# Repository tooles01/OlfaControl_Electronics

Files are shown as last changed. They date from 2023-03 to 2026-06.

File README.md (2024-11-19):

# OlfaControl_Electronics

## Full System Overview


<br>

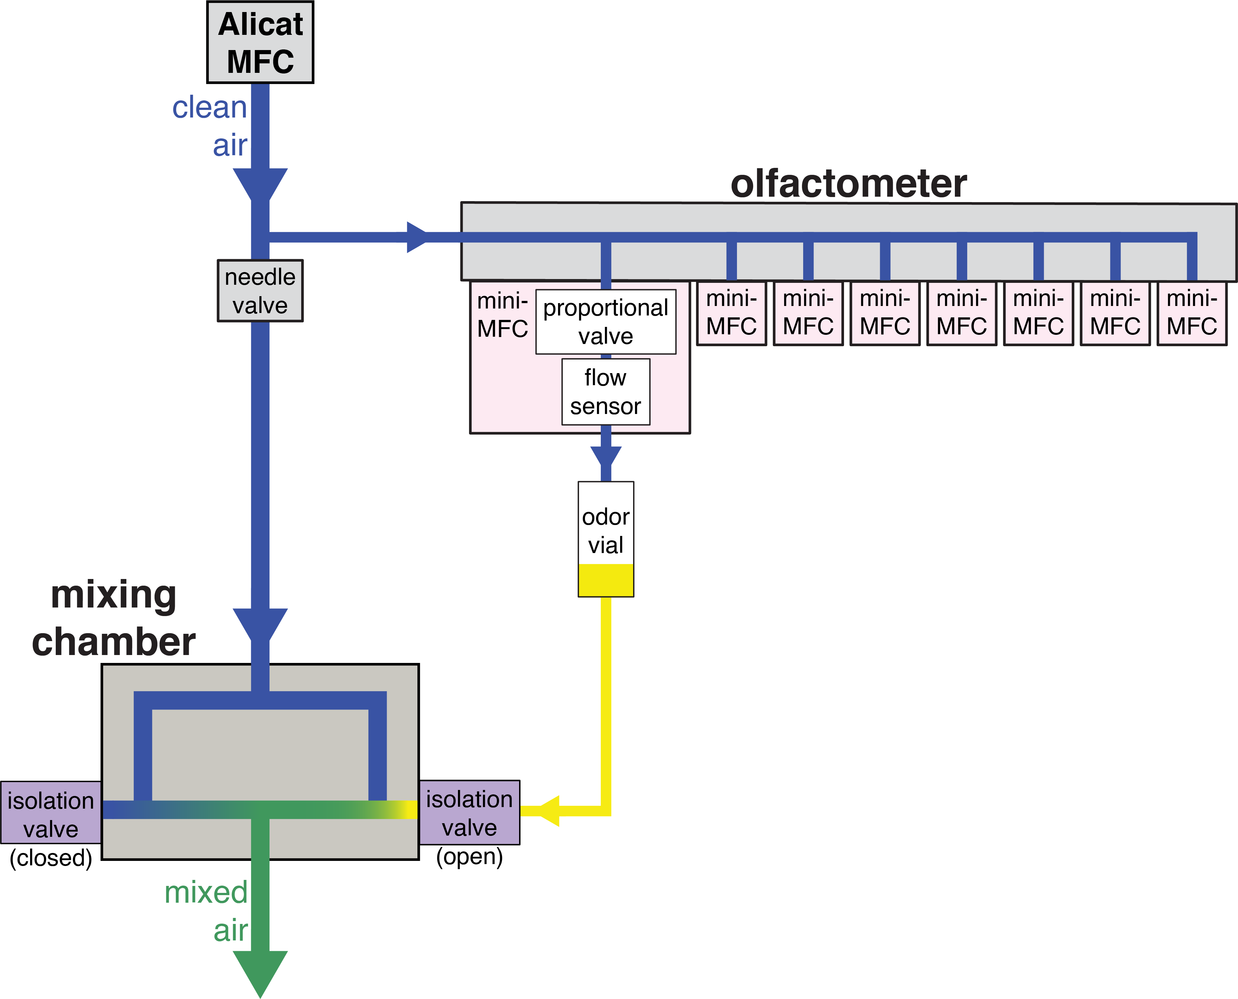
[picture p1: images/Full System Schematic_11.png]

<br>

#### Simplified:

<p align="center">
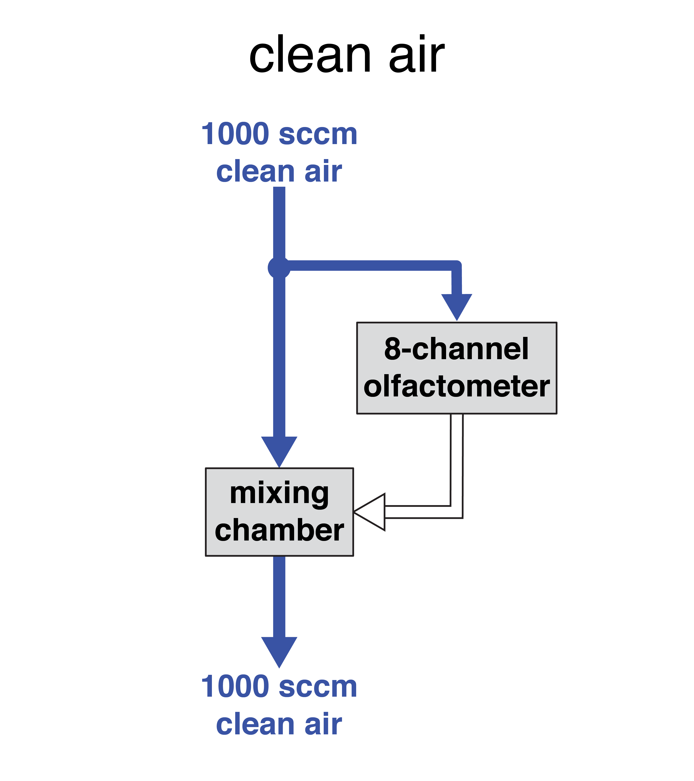
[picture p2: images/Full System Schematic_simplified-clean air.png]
  
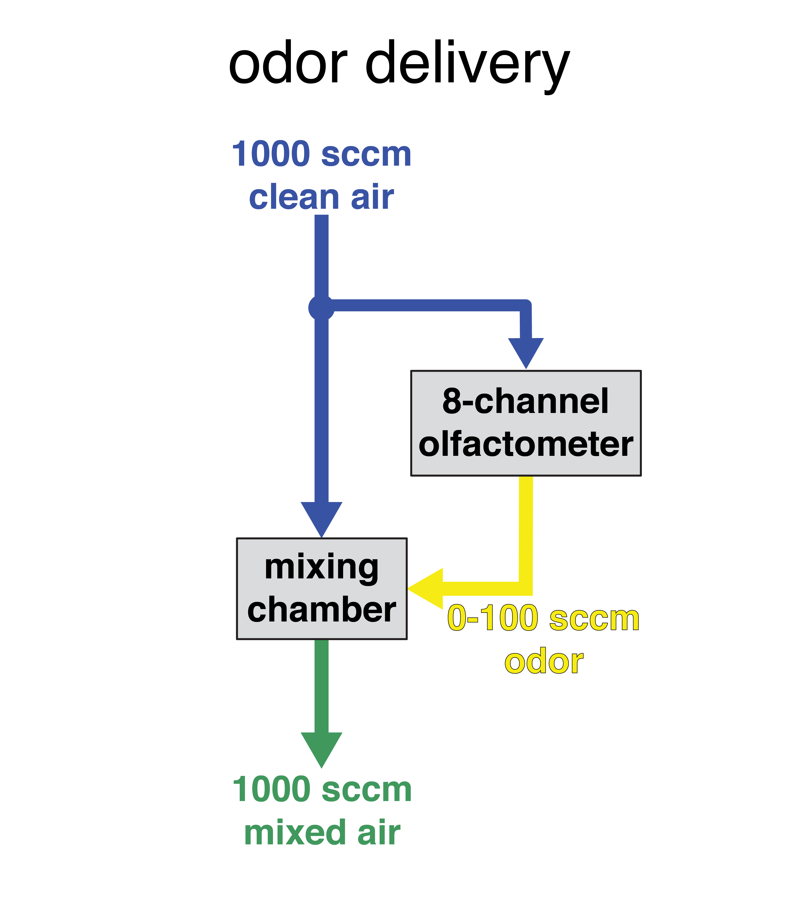
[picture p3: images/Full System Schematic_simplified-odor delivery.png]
  
</p>

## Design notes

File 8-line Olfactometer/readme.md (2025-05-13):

# 8-line Olfactometer

<br>
<p align="left">
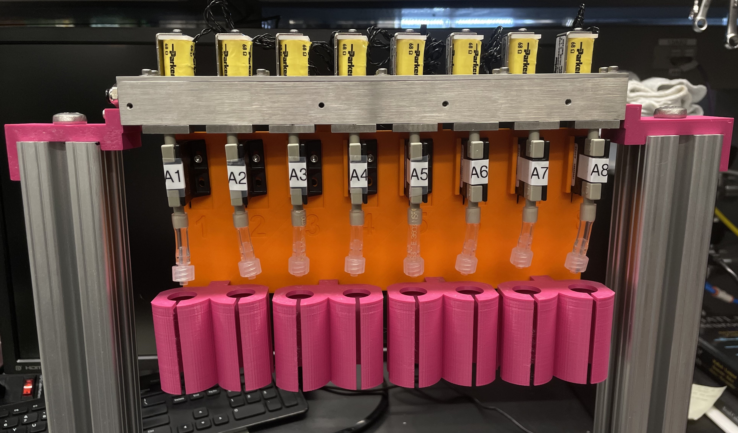
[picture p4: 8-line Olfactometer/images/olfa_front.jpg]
  
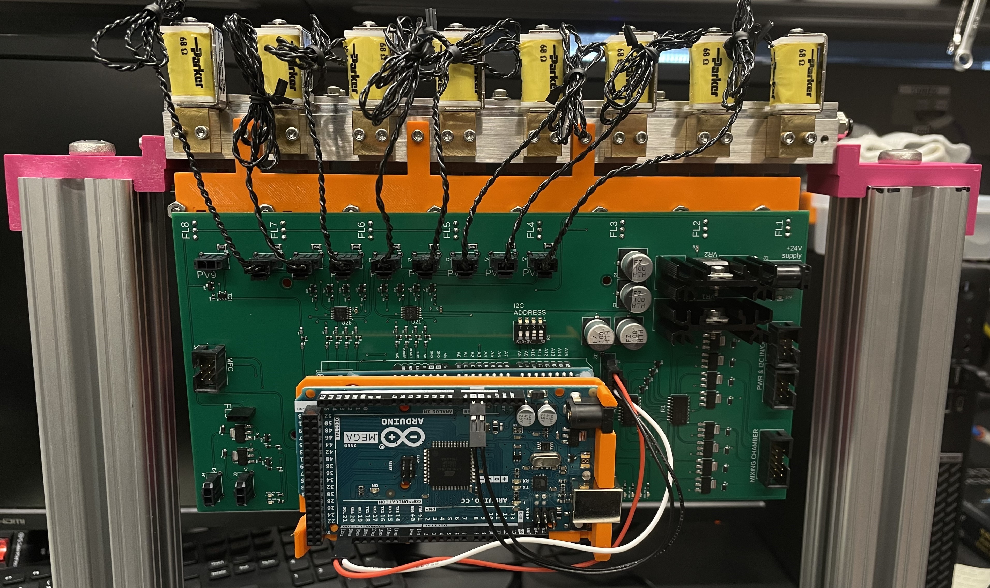
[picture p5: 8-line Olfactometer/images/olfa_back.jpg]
  
</p>

<br>
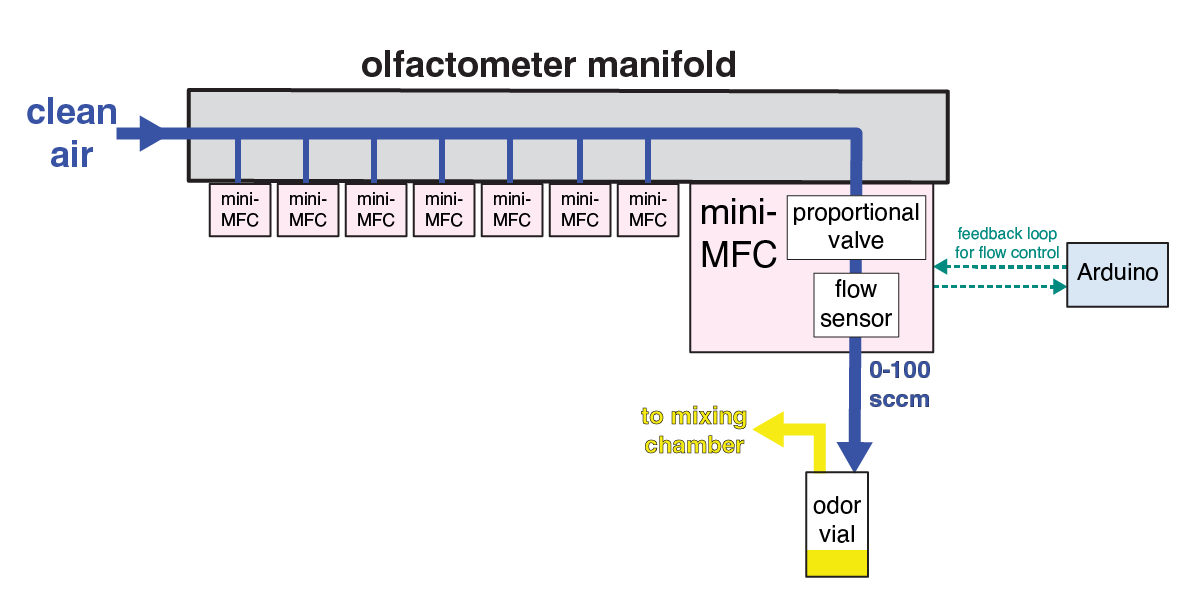
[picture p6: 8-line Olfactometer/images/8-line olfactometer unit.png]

<br>

# Parts to be manufactured
to make a single 8-line unit:
- (x1) top_cover
- (x1) main_manifold_8v
- (x8) main_manifold_cover

<br>

## updates for version 2:
- **main manifold:** mounting holes for main plate on both sides
- **main manifold cover:** 0.01" decrease in length (screw holes are now symmetric)

<br><br>

# Troubleshooting

**Problem:** Inconsistent, "squiggly" odor signal

**Diagnosis:**  Likely something (probably part of the septum) caught in the needle, blocking air flow into the vial

**Solution:** Replace vial input needle

##
**Problem:** Slow odor rise time

**Diagnosis:** Leak

**Solution:** <br>
- Ensure vial cap is on tightly
- Check that isolation valve is completely screwed in
- Replace tubing from vial to mixing chamber

##
**Problem:** Olfactometer not sending back flow values once turned on

**Solution:** <br>
If it is sending back slave addresses:
- Wait 30 seconds or so
- Click "Get Slave Addresses" 1 or 2 times
- If still a problem: Turn 24V power off and back on again, and repeat above steps

If it's not sending back slave addresses:
- Check that PCB is receiving 24V power
- Check that master Arduino I2C pins are correctly connected
- Reupload master Arduino code

##
**Problem:** Zero flow reported, even when proportional valve signal is at max (255)

**Solution:** Replace proportional valve

<!-- Troubleshooting Section as Table-->
<!--
# Troubleshooting

### Hardware/PID testing:

| Problem | Diagnosis | Solution |
| ----------- | ----------- | ----------- |
| Inconsistent, "squiggly" odor signal from PID | Likely something (probably part of the septum) caught in the needle, blocking air flow into the vial | Replace vial input needle |
| Odor signal from one line is significantly higher/lower than others | Variety of possible issues | Check if flow sensor is hitting desired setpoint. <li>If no: Recalibrate flow sensor.</li><li>If yes: Replace proportional valve</li><br>If problem persists, check for leaks.|| Slow odor rise time | Leak | <li>Ensure vial cap is on tightly.</li><li>Replace tubing from vial to mixing chamber.</li><li>Check that isolation valve is completely screwed into mixing chamber.</li>|

<br>

### Electronics/GUI:

| Problem | Solution |
| ----------- | ----------- |
| Olfactometer not sending back flow values once turned on | If it is sending back slave addresses: <li>Wait 30 seconds or so</li><li>Click "Get Slave Addresses" 1 or 2 times</li><li>If still a problem: Turn 24V power off and back on again, and repeat above steps</li><br>If it's not sending back slave addresses: <li>Check that PCB is receiving 24V power</li> <li>Check that master Arduino I2C pins are correctly connected</li><li>Re-upload master Arduino code</li>|
| Zero flow reported from flow sensor, even when proportional valve signal is at max (255) | Replace proportional valve |
-->

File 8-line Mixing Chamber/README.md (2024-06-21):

# Clippard Mixing Chamber

<p align="center">
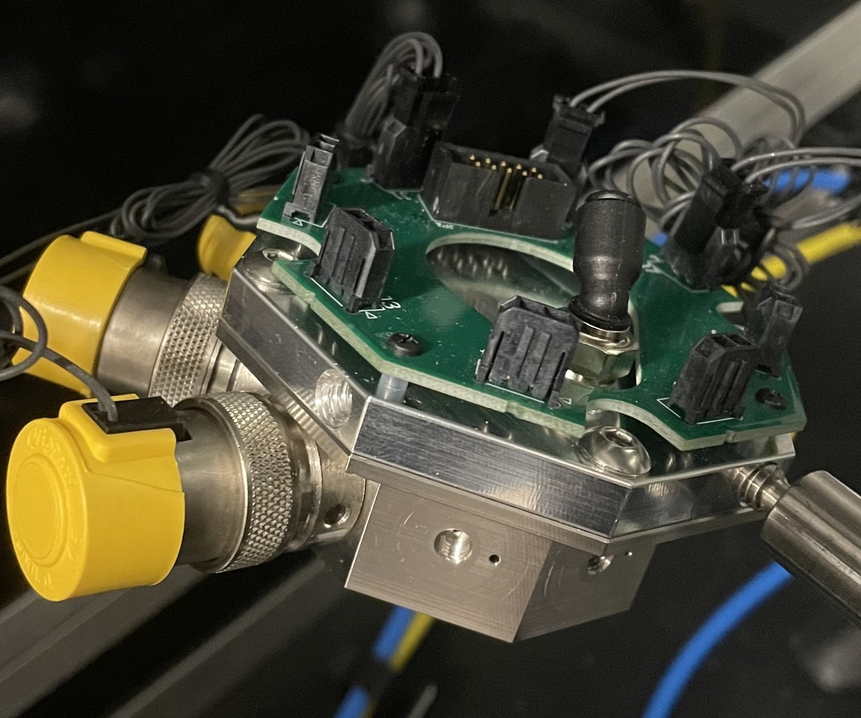
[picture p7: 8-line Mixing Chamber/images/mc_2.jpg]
  
</p>

<br>

<p align="center">
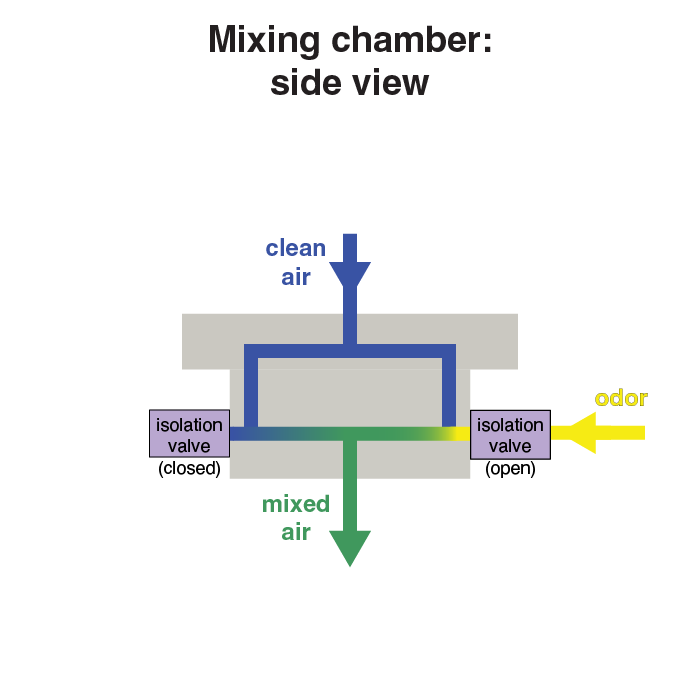
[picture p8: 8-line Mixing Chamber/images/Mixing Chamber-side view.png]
  
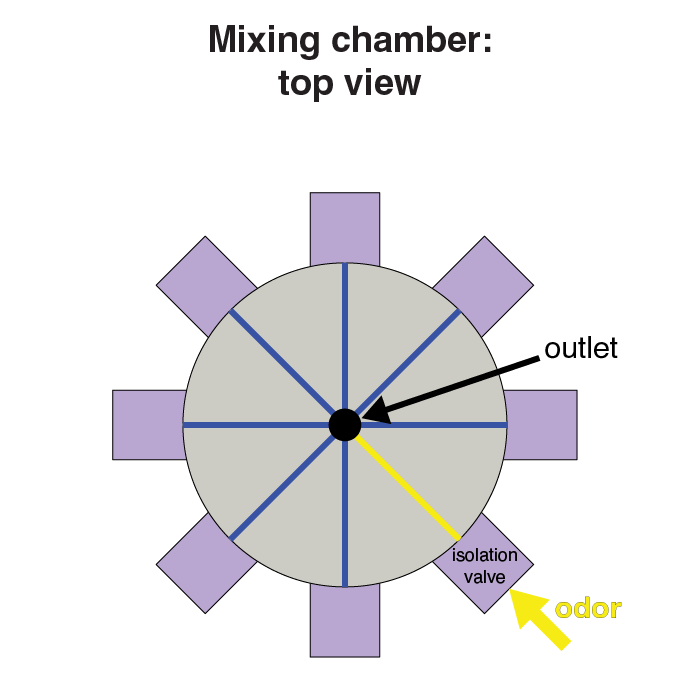
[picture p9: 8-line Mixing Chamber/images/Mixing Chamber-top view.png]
  
</p>

<br>

<p align="left">
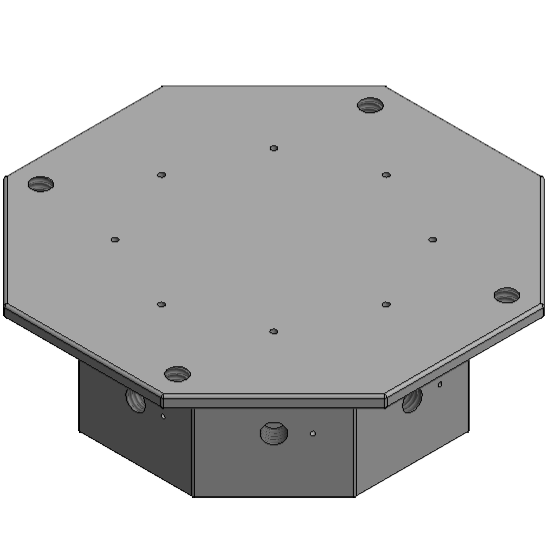
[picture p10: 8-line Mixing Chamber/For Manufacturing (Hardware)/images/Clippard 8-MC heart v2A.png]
  
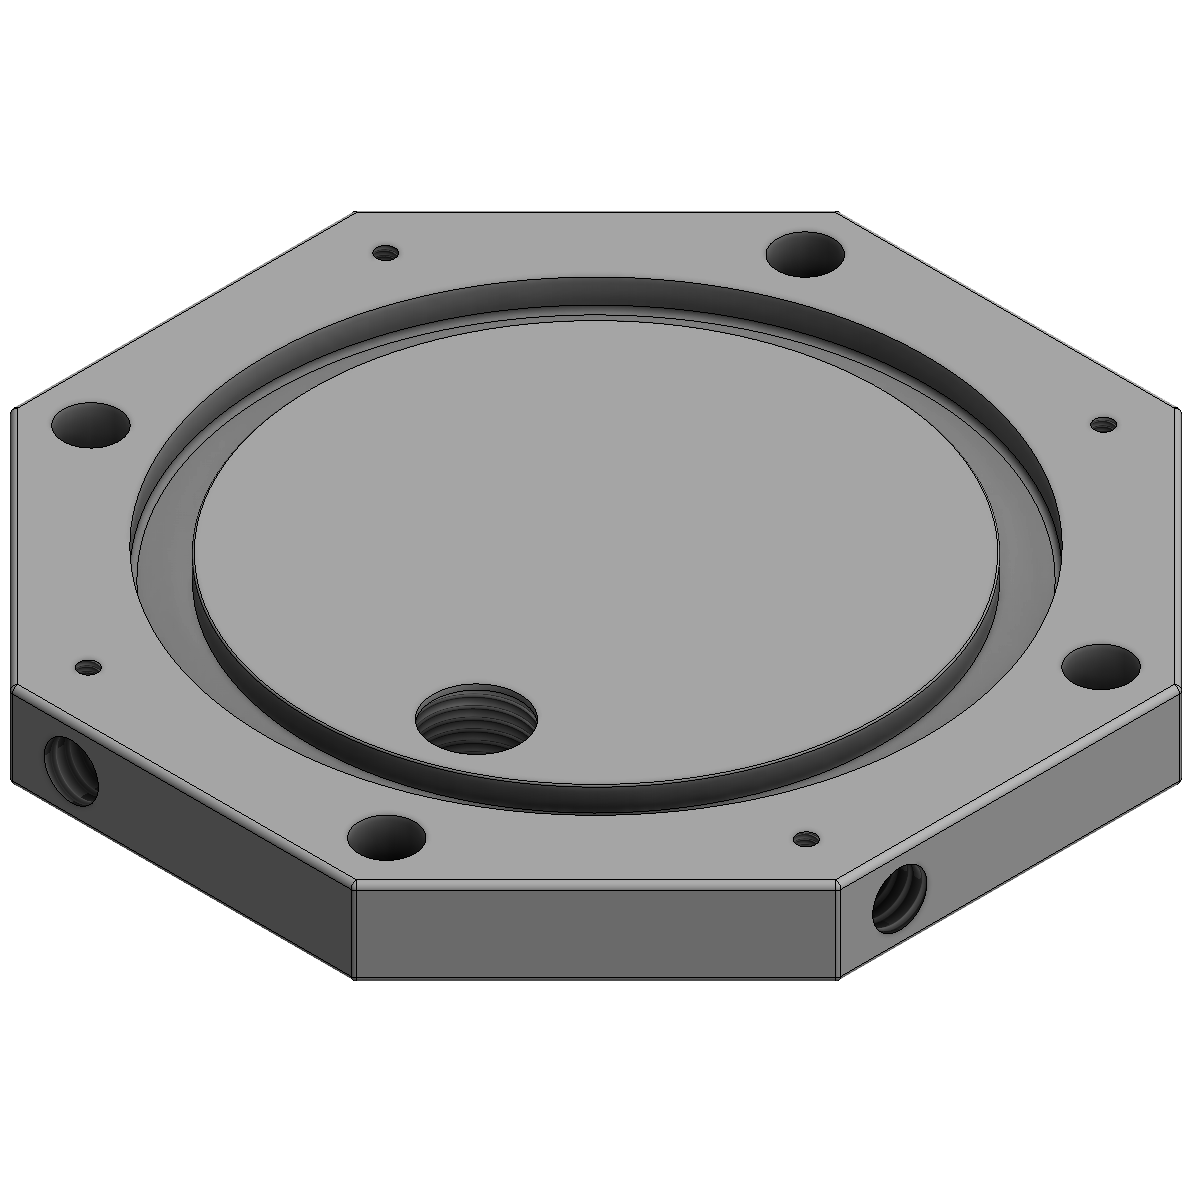
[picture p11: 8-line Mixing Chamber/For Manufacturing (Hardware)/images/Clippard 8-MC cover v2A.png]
  
</p>

<br><br>

# Parts to be manufactured

to make a single unit:

- (x1) Clippard 8-MC cover
- (x1) Clippard 8-MC heart

<br><br>

## updates for version 2:
- **Clippard 8-MC cover**
    - Slightly different location of PCB mounting holes
- **Clippard 8-MC heart**
    - Removed bottom depression, outlet changed from a male thread to an NResearch (1/4-28) female hole (matches the vial inlet holes)
    - Odor (vial) inlet ID changed
    - Odor input hole (from the bottom) was previously not aligned with its connecting inlet hole (horizontal) - tied geometries together

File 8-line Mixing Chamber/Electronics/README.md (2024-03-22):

# Clippard 8-line Mixing Chamber

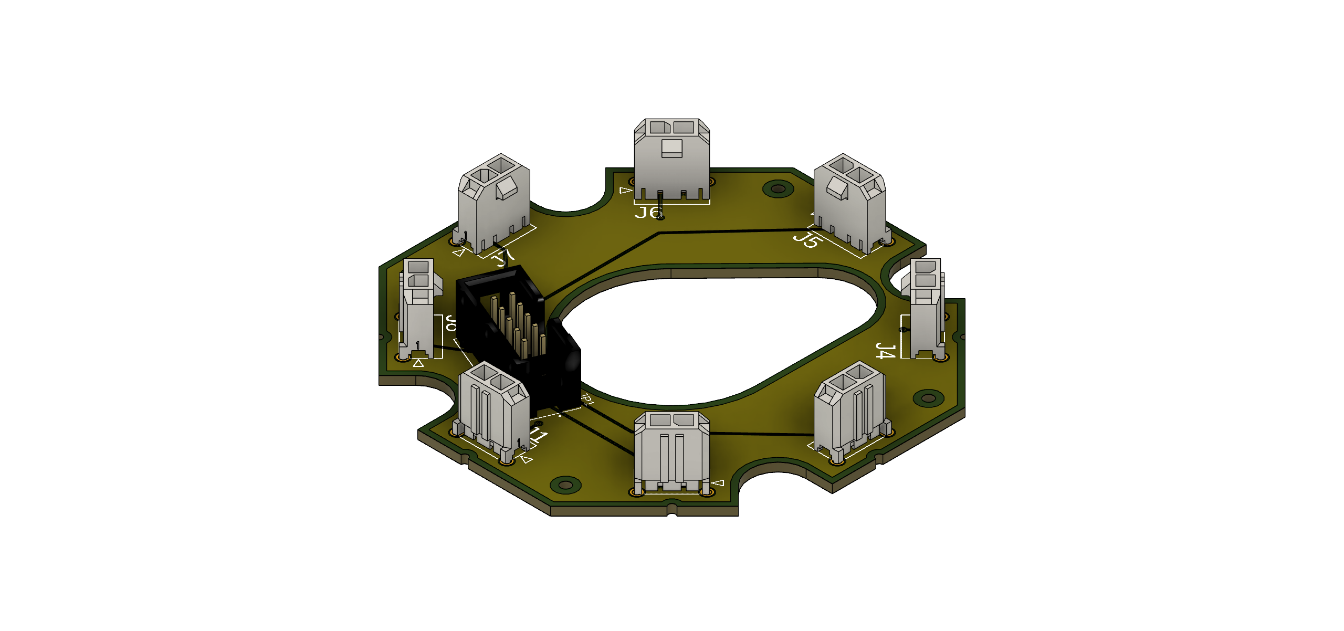
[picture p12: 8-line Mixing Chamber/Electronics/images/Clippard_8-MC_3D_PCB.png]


To be used with 8-line Olfactometer PCB (MAIN_CNTRL_v02).

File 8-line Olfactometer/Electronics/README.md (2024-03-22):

# 8-line Olfactometer

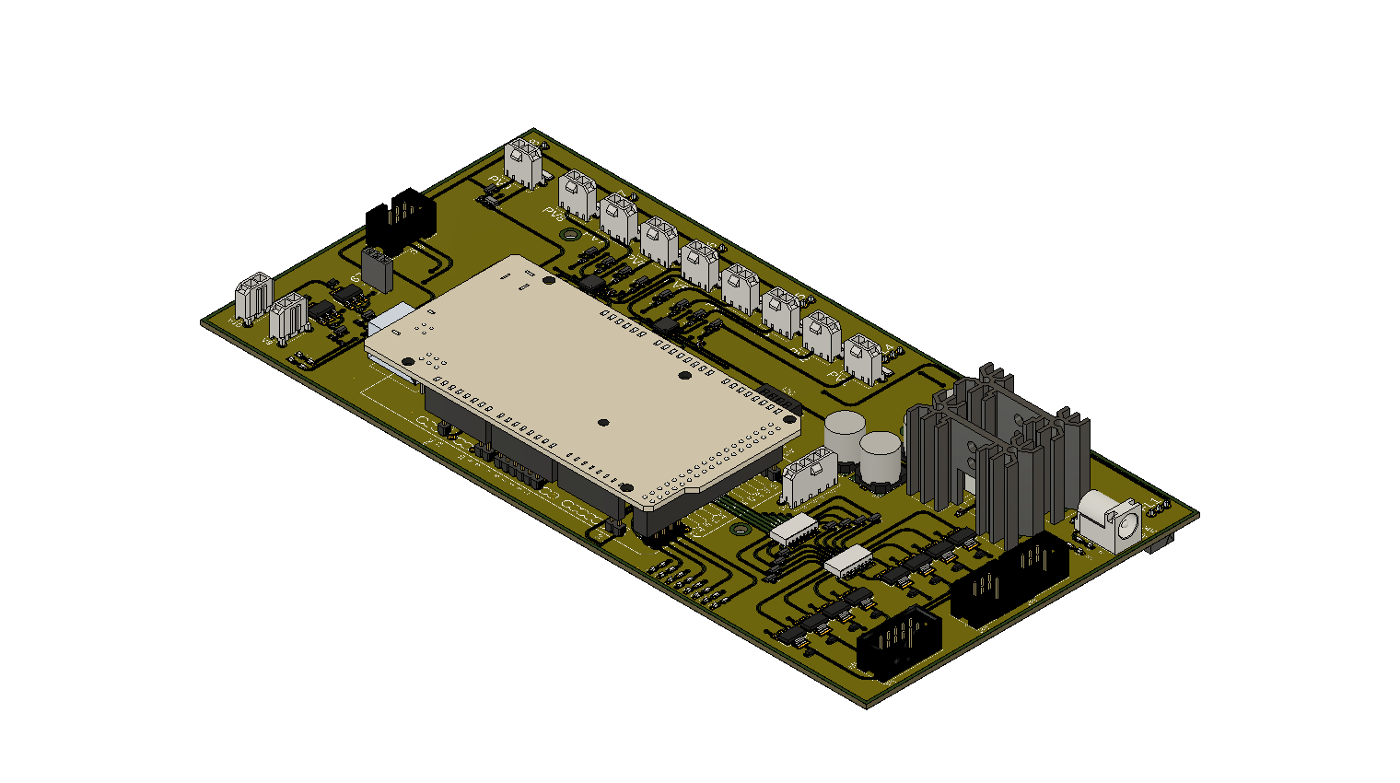
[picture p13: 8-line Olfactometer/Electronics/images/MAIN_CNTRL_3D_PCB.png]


## PCB Assembly
- Attach (x2) heat sinks to VR1 and VR2 using (x2) 4-40 x 1/4" screw and hex nut
- Solder Arduino header pins onto PCB
- Set I2C address on S1 (full dictionary of addresses is currently stored in master.ino source code)
- Connect master Arduino
    - Make a wire to connect from J2 (4pos Molex female) to master Arduino pins (Dupont male wires). Connect to SDA, SCL, GND and GND.
    - (Mount master Arduino on top using Arduino holder 3D printed part)

<br><br><br>

## updates for version 2:

### power:
- single 24V power supply (instead of 1x 24V supply and 1x 10V supply)
    - voltage regulators & corresponding circuitry to shift down to 10V for the components that need it
    - (2 voltage regulators + heat sinks to prevent overheating when multiple lines activated at once)

### error fixes:
- fixes (x4) incorrectly wired proportional valves
- removes connection between isolation valves 3 & 8

### other:
- multiple boards can be chained together by a single ribbon cable, which carries the power and I2C lines
    - (only 1 board in the chain needs a 24V input, the rest receive power through the ribbon cable)
- updated header for connecting to mixing chamber (standard 10pos IDC cable)

### new components:
- (x8) LEDs to indicate isolation valve activated
- (x2) LEDs to indicate power (10V, 24V)
- (x1) connection for additional flow sensor
- (x1) connection for additional proportional valve
- (x2) connection for additional isolation valve
- (x1) connection for Alicat MFC

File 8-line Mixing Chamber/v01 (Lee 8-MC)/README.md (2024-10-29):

# Lee Mixing Chamber

<p align="left">
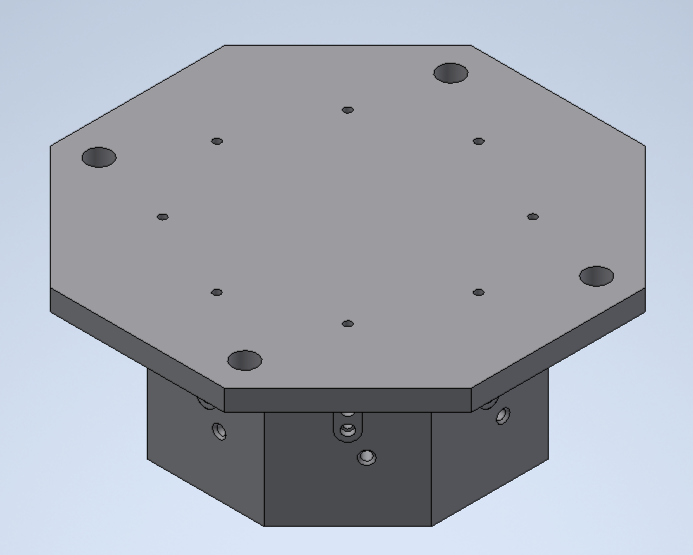
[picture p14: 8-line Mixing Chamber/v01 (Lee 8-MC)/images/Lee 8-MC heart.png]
  
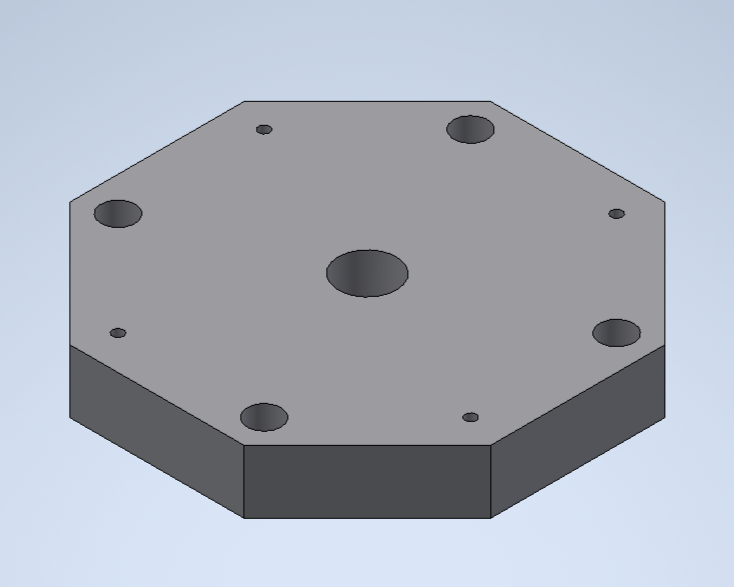
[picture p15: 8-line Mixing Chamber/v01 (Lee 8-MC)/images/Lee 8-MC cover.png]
  
</p>

<br><br>

# Parts to be manufactured

to make a single unit:

- (x1) Lee 8-MC cover
- (x1) Lee 8-MC heart

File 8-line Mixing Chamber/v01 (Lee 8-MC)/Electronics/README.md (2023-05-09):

# Lee 8-line Mixing Chamber

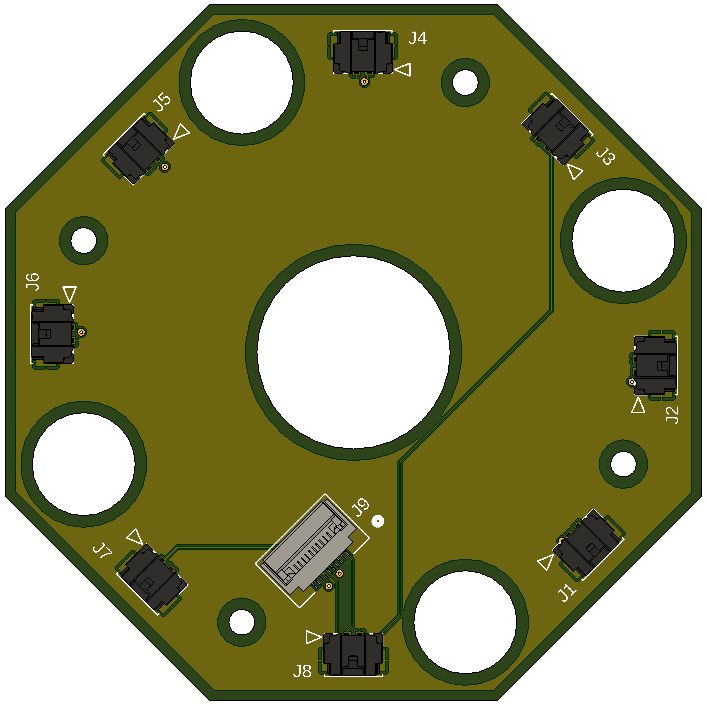
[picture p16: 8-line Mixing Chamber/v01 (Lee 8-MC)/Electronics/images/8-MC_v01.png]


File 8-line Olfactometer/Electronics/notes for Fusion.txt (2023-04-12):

Fusion file names:

MAIN CNTRL v01

schematic:	MAIN CNTRL_v3 v8
board:		MAIN_CNTRL_v3_v217
3D PCB:		MAIN_CNTRL_v3 v140
screenshot:	MAIN_CNTRL_v3 v140

MAIN CNTRL V02

schematic:	MAIN_CNTRL_v2_v166
board:		MAIN CNTRL_v2 v183
3D PCB:		MAIN CNTRL_v2 v14
screenshot:	MAIN CNTRL_v2 v14

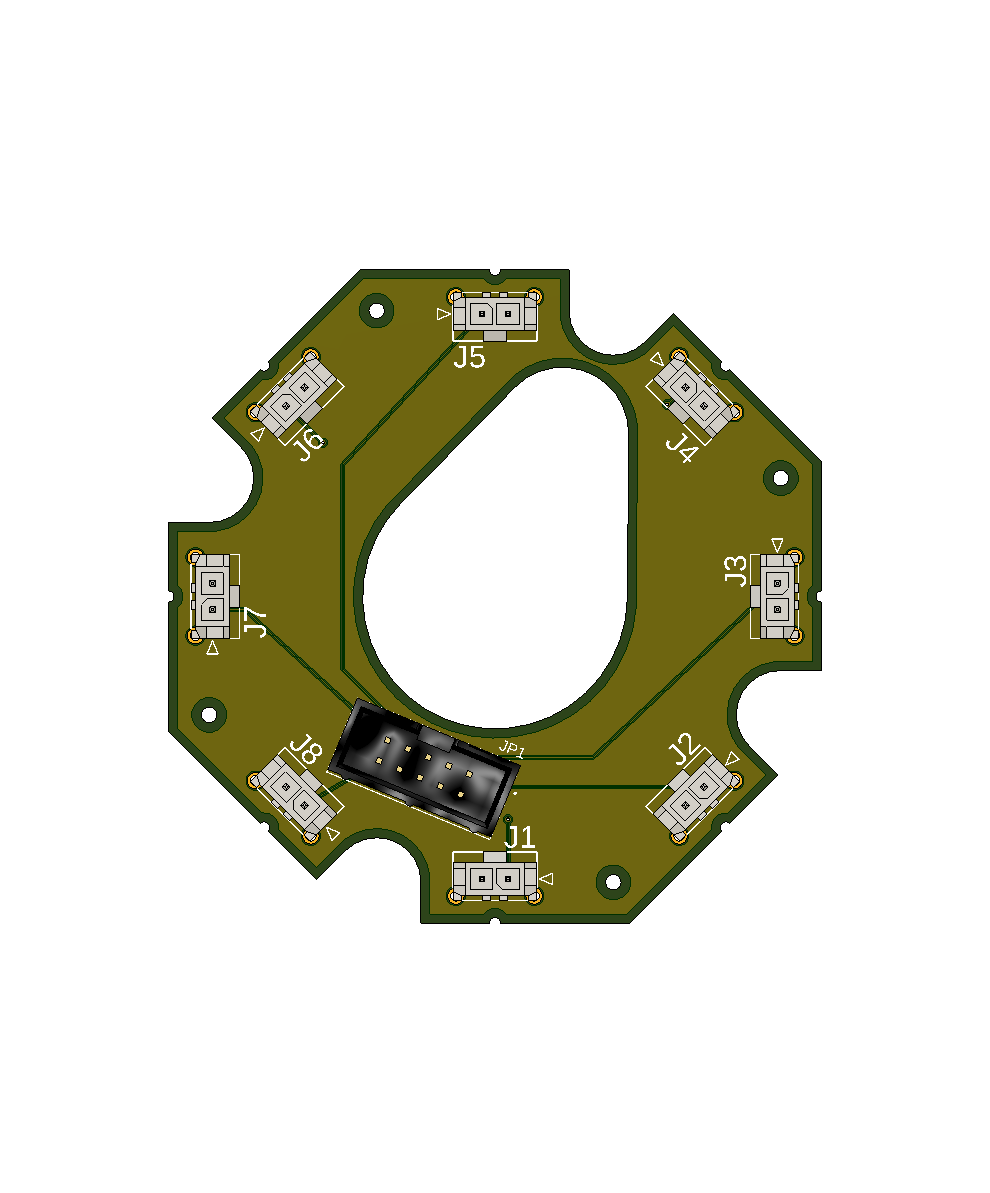
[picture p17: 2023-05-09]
8-line Mixing Chamber/Electronics/images/Clippard 8-MC 3D PCB_top.png

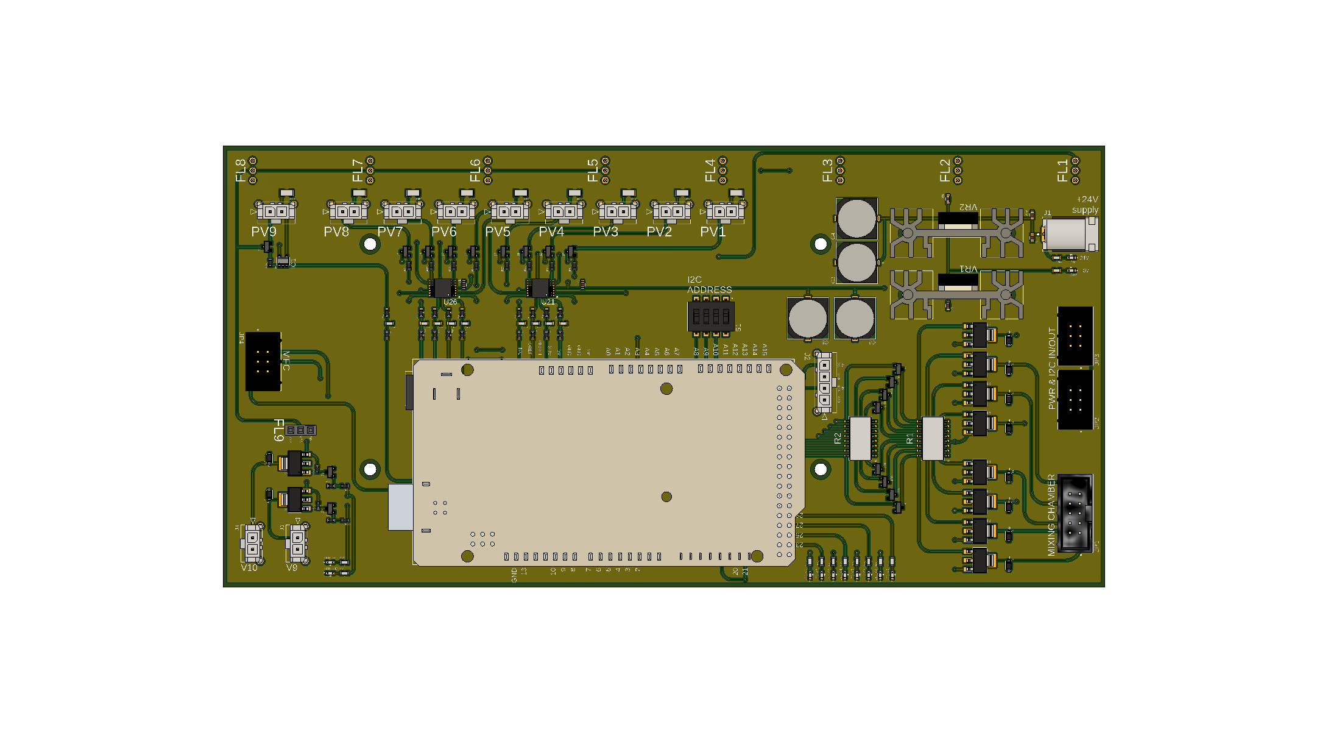
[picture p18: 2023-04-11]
8-line Olfactometer/Electronics/images/MAIN CNTRL 3D PCB_top.png

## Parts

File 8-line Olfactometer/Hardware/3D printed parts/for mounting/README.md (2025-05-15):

### for mounting with sliding or standing setup
Hole (for mounting with standing setup) will fit M8 or 5/16" screw

<br>

<!--BigAssembly_01_8020_1515.iam-->
**mount_bracket 8020_1515_withhole**  
Fits on 1.5" profiles from 8020
<p align="center">
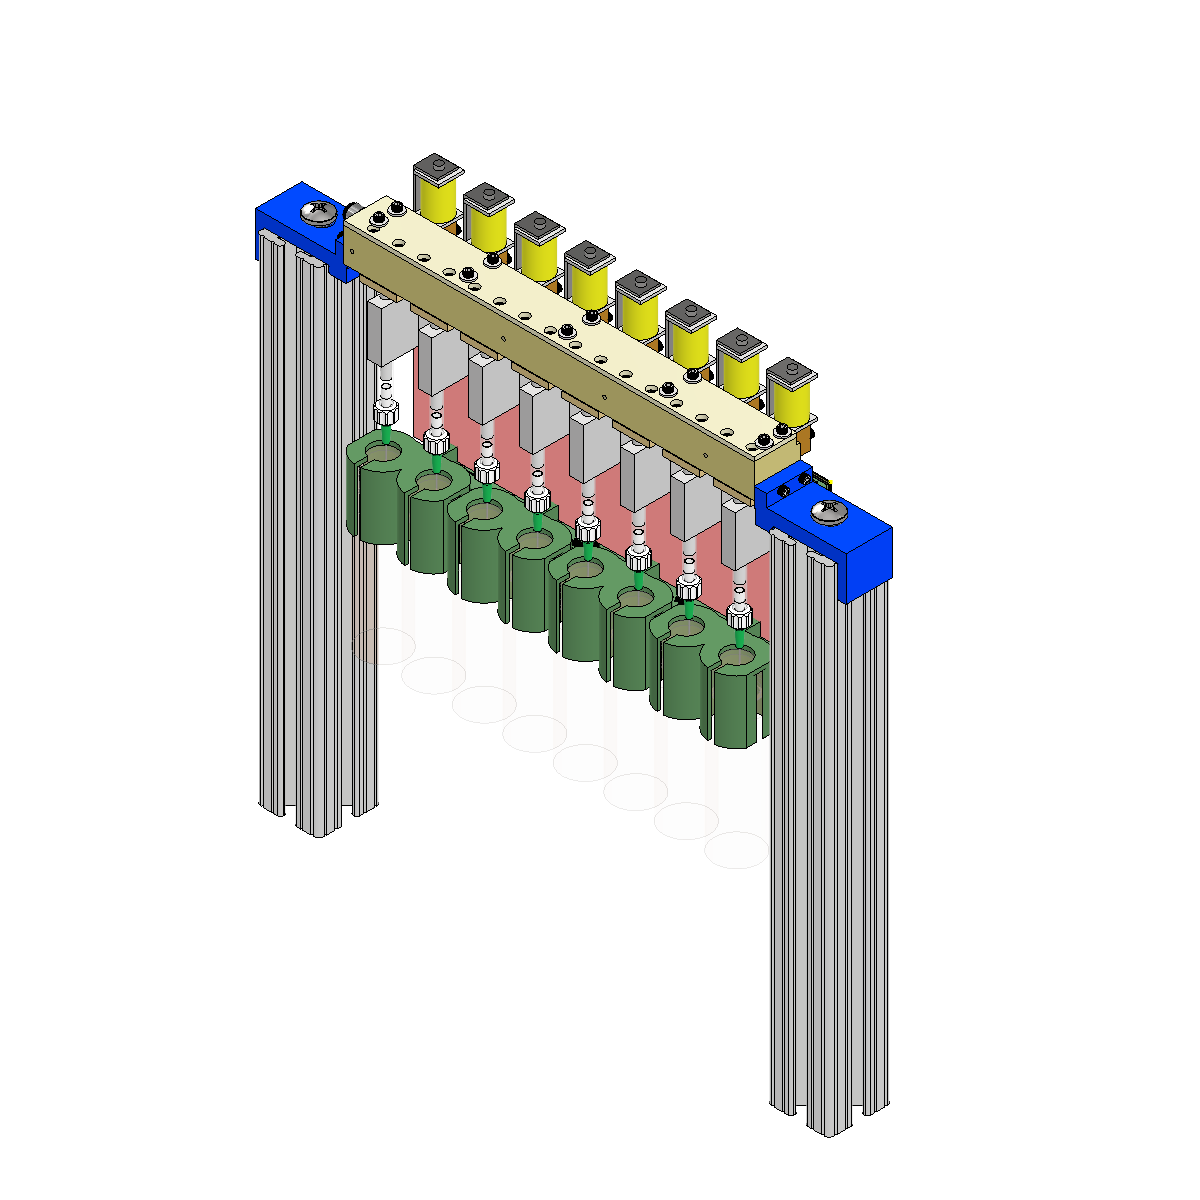
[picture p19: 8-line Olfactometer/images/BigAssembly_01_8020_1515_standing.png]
  
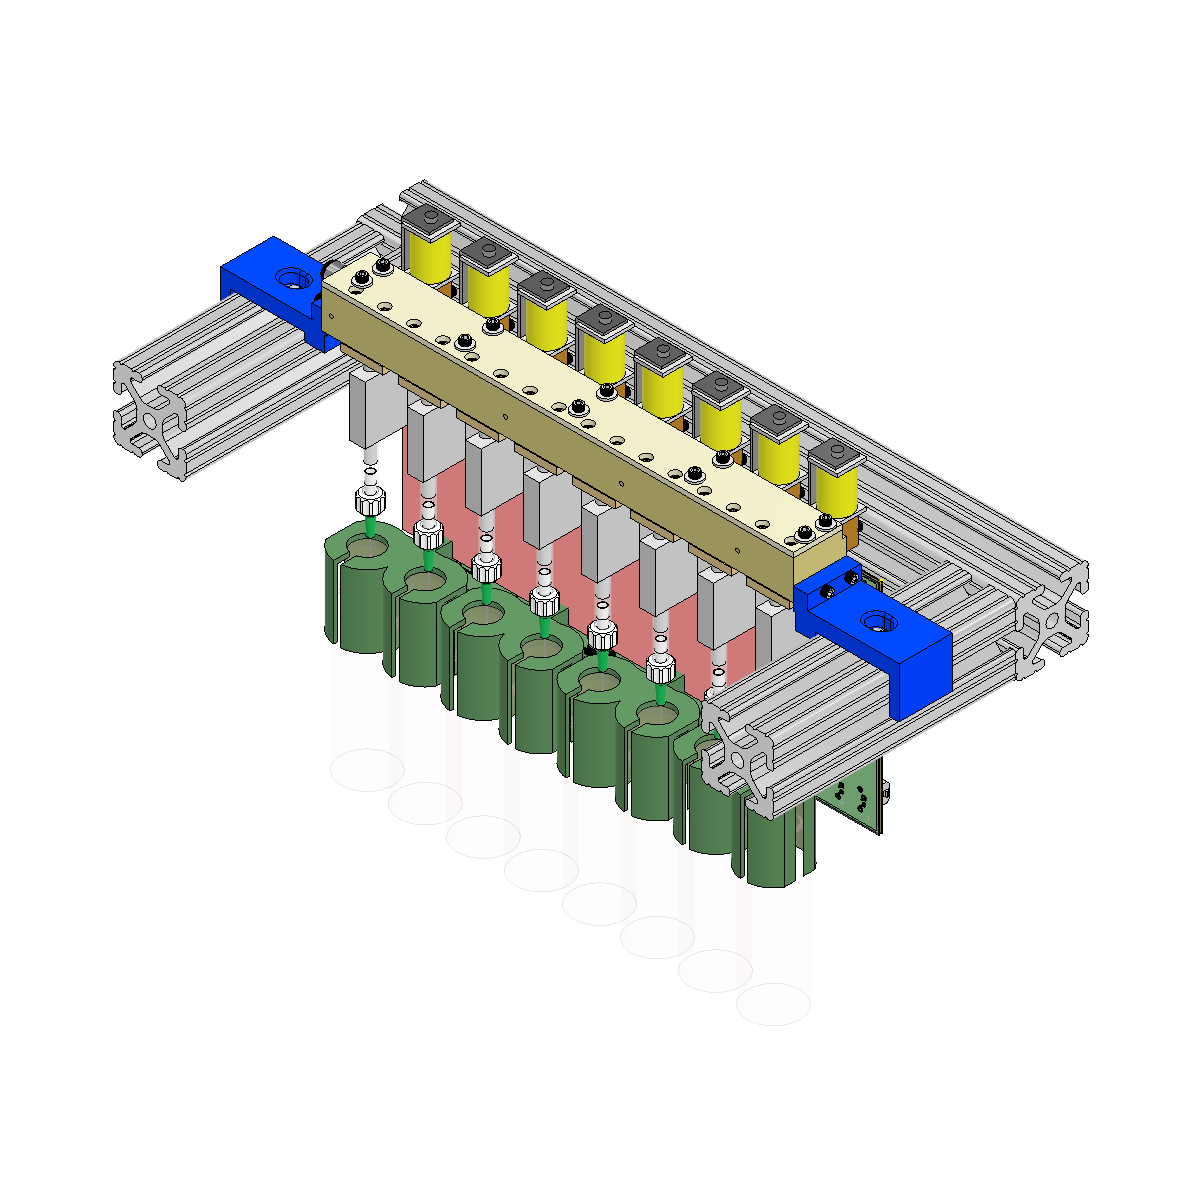
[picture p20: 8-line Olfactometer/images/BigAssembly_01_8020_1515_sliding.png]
  
</p>
<br>

<!--BigAssembly_01_item_8.iam-->
**mount_bracket item_8_withhole**  
Fits on 40mm profiles from item
<p align="center">
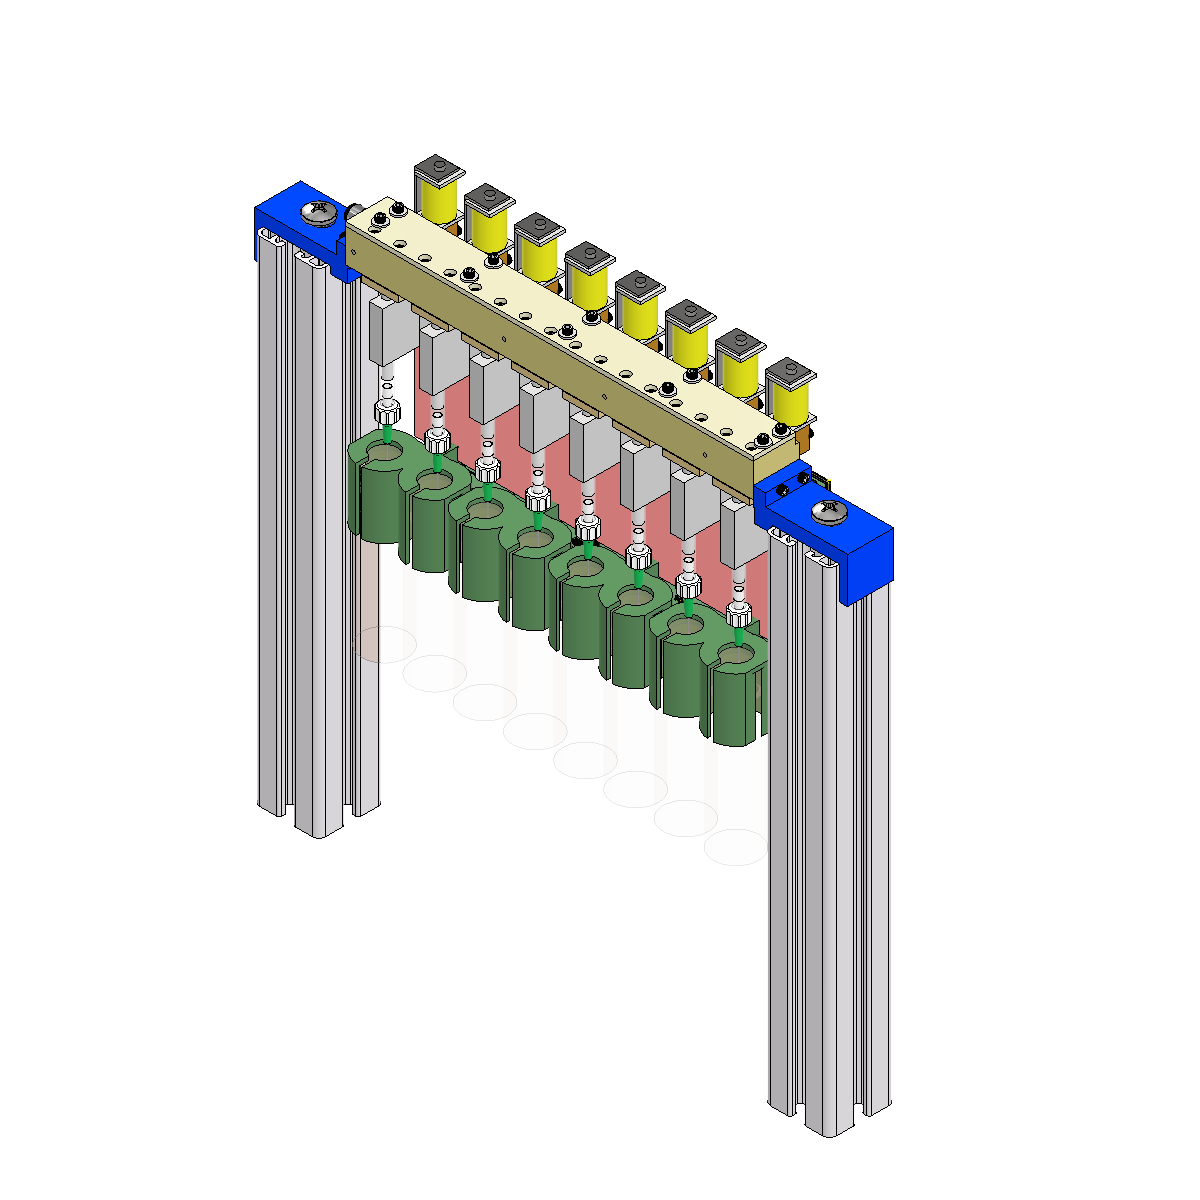
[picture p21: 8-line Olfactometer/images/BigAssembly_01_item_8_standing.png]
  
</p>
<!--
## TODO:
- add sliding setup for item
- add links to item and 8020 profiles
-->

#
### Current setup in Mainland lab:
<!--BigAssembly_02.iam-->
**mount_left**  
**mount_right**  
Mounted using 40mm profiles from item, M8 screws

<p align="center">
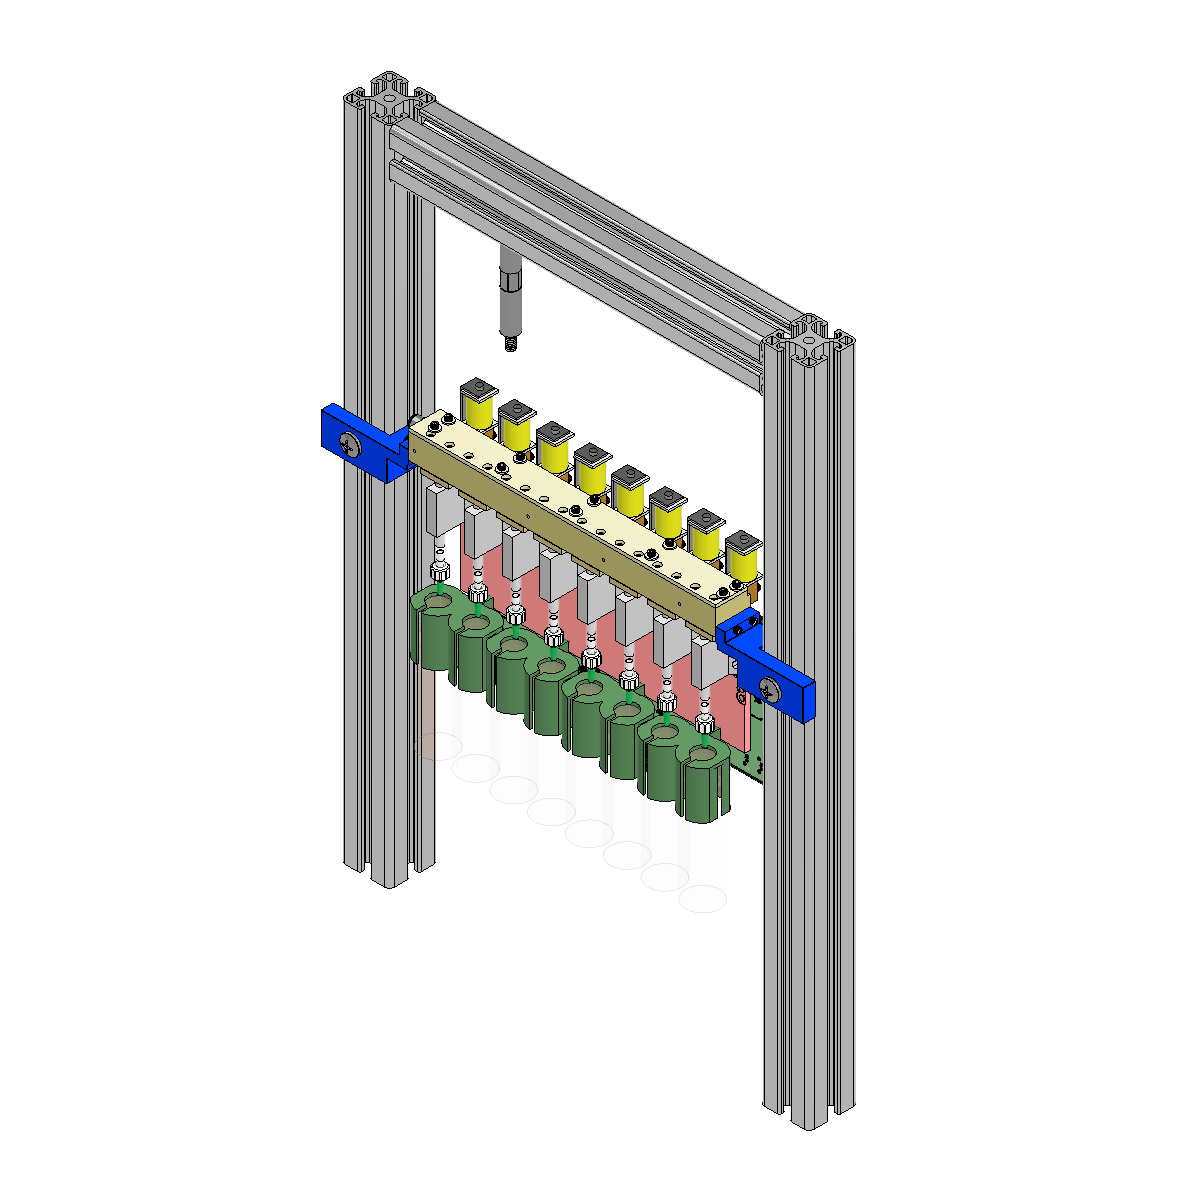
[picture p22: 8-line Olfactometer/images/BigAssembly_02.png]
  
</p>

<!-- 
For mounting with sliding setup only:

**mount_bracket 8020_1515**
Fits on 1.5" profiles from 8020

**mount_bracket item_5**
Fits on 20mm profiles from item
-->

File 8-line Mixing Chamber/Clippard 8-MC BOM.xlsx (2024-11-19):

Item # | Qty |  | Description | Manufacturer | Manuf. Part #
1 | 1 | Clippard 8-MC heart v2A | Clippard 8-valve Mixing Chamber Heart | Custom Machined Part | n/a
2 | 1 | Clippard 8-MC cover v2A | Clippard 8-valve Mixing Chamber Cover | Custom Machined Part | n/a
3 | 1 | #227 O-ring | O-ring for sealing MC heart & cover | McMaster-Carr | 5267T193 (https://www1.mcmaster.com/5267T193/)
4 | 1 | Input fitting | 1/8 NPT x 1/8" Tube OD Push-To-Connect Fitting | McMaster-Carr | 5779K102 (https://www1.mcmaster.com/5779K102/)
5 | 8 | Isolation valves | Clippard 24V Isolation Valves | Clippard | EV-2M-24-V (https://www.clippard.com/part/EV-2M-24-V)
6 | 4 | 10-24 x 1/2" screws | 18-8 Stainless Steel Button Head Hex Drive Screw 10-24 Thread Size, 1/2" Long | McMaster-Carr | 92949A242 (https://www1.mcmaster.com/92949A242/)
7 | 1 | Clippard 8-MC PCB | Clippard 8-valve Mixing Chamber PCB | Custom PCB | n/a
8 | 4 | 1/8" spacers | Off-White Nylon Unthreaded Spacer 1/8" OD, 1/8" Long, for Number 2 Screw Size | McMaster-Carr | 94639A460 (https://www1.mcmaster.com/94639A460/)
9 | 4 | 2-56 x 1/4"screws | Nylon Pan Head Screws Phillips, 2-56 Thread, 1/4" Long | McMaster-Carr | 94735A707 (https://www1.mcmaster.com/94735A707-94735A124/)

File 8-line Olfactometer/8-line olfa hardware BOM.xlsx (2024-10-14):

 | Item # | Qty |  | Description | Manufacturer | Part # | cost / pack | pack size
main manifold to top cover | 6 | 1 | Input fitting | Push-to-Connect Tube Fitting for Air; Straight Adapter, for 1/4" Tube OD x 1/8 NPT Male | McMaster-Carr | 5779K108 (https://www1.mcmaster.com/5779K108/) | $5.49 | each
 | 1 | 1 | main_manifold_8v_v02 | 8-line Olfactometer Main Manifold | Custom Machined Part | n/a
 | 2 | 1 | top_cover_02 | 8-line Olfactometer Top Cover | Custom Machined Part | n/a
 | 3 | 1 | #051 O-ring | Chemical-Resistant Viton® Fluoroelastomer O-Ring; 1/16 Fractional Width, Dash Number 051 | McMaster-Carr | 9464K721 (https://www1.mcmaster.com/9464K721/) | $16.61 | each | * ordered -051 size, might be -052 tho
 | 4 | 10 | 4-40 x 1/4" screws | 18-8 Stainless Steel Socket Head Screw 4-40 Thread Size, 1/4" Long | McMaster-Carr | 92196A106 (https://www1.mcmaster.com/92196A106/) | $3.92 | 100 pack
 | 5 | 10 | 4-40 washers | 18-8 Stainless Steel Washer for Number 4 Screw Size, 0.125" ID, 0.312" OD | McMaster-Carr | 92141A005 (https://www1.mcmaster.com/92141A005/) | $1.43 | 100 pack
prop valves to main manifold | 7 | 8 | Proportional Valves | VSO Low Flow Miniature Proportional Valve | Parker | 910-000200-002
 | 8 | 16 | FKM O-rings | O-ring, FKM, 0.114" ID x 0.070" Thick | Parker | 190-007024-002
 | 9 | 16 | 4-40 x 5/8" screws | Screw 4-40 x 5/8" Pan Head | Parker | 191-000115-010
main plate | 10 | 1 | mainPlate | Main Plate for mounting olfactometer | 3D printed | n/a
 | 11 | 3 | 4-40 x 1/4" screw | 18-8 Stainless Steel Socket Head Screw 4-40 Thread Size, 1/4" Long | McMaster-Carr | 92196A106 (https://www1.mcmaster.com/92196A106/) | $5.74 | 100 pack
flow sensors | 12 | 8 | Flow Sensors | Air Flow Sensor 200sccm Male, 0.2" (5.08mm) Plastic | Honeywell | AWM3100V
 | 13 |  | 1/8" ID 1/4" OD tubing | 1/8" ID x 1/4" OD x 1/16" Wall Tygon® S3™ E-3603 Laboratory Tubing | United States Plastic Corp. | 57631 | $9.50 | 10 feet
 | 14 | 8 | Male luer to 1/8" barb | Idex Barbed Luer Adapter, Polypropylene, 0.080" Bore, Female Luer Lock x 1/8" Hose Barb | IDEX | P-859 (https://www.coleparmer.com/i/idex-barbed-luer-adapter-polypropylene-0-080-bore-female-luer-lock-x-1-8-hose-barb-1-ea/0202406?searchterm=p-859) | $1.30 | each
 | 15 | 8 | #008 O-rings | Chemical-Resistant Viton® Fluoroelastomer O-Ring 1/16 Fractional Width, Dash Number 008 | McMaster-Carr | 9464K13 (https://www1.mcmaster.com/9464K13/) | $8.50 | 100 pack
 | 16 | 8 | main_manifold_cover_1v_v02 | 8-line Olfactometer Main Manifold Cover | Custom Machined Part | n/a
 | 17 | 16 | 4-40 x 7/8" screws | 18-8 Stainless Steel Socket Head Screw 4-40 Thread Size, 7/8" Long | McMaster-Carr | 92196A114 (https://www1.mcmaster.com/92196A114/) | $7.88 | 100 pack
 | 18 | 8 | 4-40 x 3/8" screws | 18-8 Stainless Steel Socket Head Screw 4-40 Thread Size, 3/8" Long | McMaster-Carr | 92196A108 (https://www1.mcmaster.com/92196A108/) | $6.07 | 100 pack
 | 19 | 8 | 4-40 hex nuts | 18-8 Stainless Steel Hex Nut 4-40 Thread Size | McMaster-Carr | 91841A005 (https://www1.mcmaster.com/91841A005/) | $3.89 | 100 pack
for mounting | 20 | 2 | 3d printed mount |  | 3D printed | n/a
 | 21 | 4 | 4-40 x 1/2" screws | 18-8 Stainless Steel Socket Head Screw 4-40 Thread Size, 1/2" Long | McMaster-Carr | 92196A110 (https://www1.mcmaster.com/92196A110/) | $6.38 | 100 pack
 | 22 | 2 | M8 screws
vial holders | 23 | 4 | vialHolder_2v | Vial Holder | 3D printed | n/a
 | 24 | 4 | 4-40 Heat-set inserts | Tapered Heat-Set Inserts for Plastic 4-40 Thread Size, 0.135" Installed Length, Brass | McMaster-Carr | 93365A120 (https://www1.mcmaster.com/93365A120/) | $14.11 | 100 pack
 | 25 | 4 | 4-40 x 3/8" screws | 18-8 Stainless Steel Socket Head Screw 4-40 Thread Size, 3/8" Long | McMaster-Carr | 92196A108 (https://www1.mcmaster.com/92196A108/) | $6.07 | 100 pack
flow sensor to vial | 26 | 8 | 21G Needles | PrecisionGlide Hypodermic Needle 21gx2" Green | Becton-Dickinson | 305129 (https://www.henryschein.com/us-en/medical/p/medical-surgical-supplies/hypodermic-supplies/needle-disposable/9879426) | $20.00 | 100/Bx
vial to mixing chamber | 27 | 8 | Odor Vials | Precleaned Volatile Organic Analyte Sampling Vials, 40 mL, 24-400 Screw-Thread | Restek | 21797 (https://www.restek.com/p/21797) | $122.00 | 72 pack
 | 28 | 8 | Fittings & Ferrules | 1/4-28 Two Piece Fitting Set | NResearch | 252P109 (https://www.nresearch.com/) | $161.68 | 50 pack
 | 29 | 8 | 1/32" ID x 1/16" OD tubing | Masterflex® Transfer Tubing, PTFE, 1/32" ID x 1/16 " OD | Masterflex | 06407-41 (https://us.vwr.com/store/item/NA5133589/masterflex-transfer-tubing-polytetrafluoroethylene-ptfe-avantor)

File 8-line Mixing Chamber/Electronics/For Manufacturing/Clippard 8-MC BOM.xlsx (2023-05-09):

Item # | Designator | Qty | Manufacturer | Mfg Part # | Description / Value | Package / Footprint | Type | Instructions / Notes
1 | JP1 | 1 | TE Connectivity AMP Connectors | 1761681-3 | Connector Header Through Hole 10 position 0.100 (2.54mm)" |  | Through Hole
2 | J1, J2, J3, J4, J5, J6, J7, J8 | 8 | Molex | 0436500215 | Connector Header Through Hole 2 position 0.118 (3.00mm)" |  | Through Hole

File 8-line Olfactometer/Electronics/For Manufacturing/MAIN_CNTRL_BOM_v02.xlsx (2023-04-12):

Item # | Designator | Qty | Manufacturer | Mfg. Part # | Distributor | Distrib. Part # | Description | Package/Footprint | Type | Notes
1 | C1, C2, C7, C8 | 4 | TDK Corporation | CGA3E2X7R1H104M080AD | Digi-Key | 445-9834-1-ND | Capacitor 0.1 µF ±20% 50V Ceramic Capacitor | 0603 (1608 Metric) | Surface Mount
2 | C3, C4, C5, C6 | 4 | Rubycon | 50THV100M10X10.5 | Digi-Key | 1189-2059-1-ND | Capacitor 100 µF ±20% 50V Aluminum Electrolytic Capacitor | Radial, Can - SMD | Surface Mount
3 | C9, C10 | 2 | TDK | CGA3E2X7R1H103K080AE | Digi-Key | 445-15955-1-ND | Capacitor 10000 pF ±10% 50V Ceramic Capacitor | 0603 (1608 Metric) | Surface Mount
4 | D1, D2, D3, D4, D5, D6, D7, D8, D9, D10 | 10 | ROHM Semiconductor | RB168VYM150FHTR | Digi-Key | RB168VYM150FHCT-ND | Diode Schottky 150 V 1A | 2-SMD, Flat Lead | Surface Mount
5 | FL1, FL2, FL3, FL4, FL5, FL6, FL7, FL8, FL9 | 9 | Sullins Connector Solutions | PPPC031LFBN-RC | Digi-Key | S7036-ND | 3 Position Header Connector 0.100 (2.54mm) Through Hole Gold" |  | Through Hole
6 | HS1, HS2 | 2 | Assmann WSW Components | V8813W | Digi-Key | AE10771-ND | Heat Sink SOT-32, TO-220, TOP-3 Aluminum Board Level, Vertical |  | Through Hole
7 | IC1 | 1 | STMicroelectronics | TS321AILT | Digi-Key | 497-8093-1-ND | General Purpose Amplifier 1 Circuit | SOT-23-5 | Surface Mount
8 | J1 | 1 | CUI Devices | PJ-037AH | Digi-Key | CP-037AH-ND | DC Power Jack Connector 2.0 x 6.5 mm, 5.0 A |  | Through Hole
9 | JP2, JP3, JP4 | 3 | TE Connectivity AMP Connectors | 1761681-1 | Digi-Key | A122759-ND | Connector Header Through Hole 6 position 0.100 (2.54mm)" |  | Through Hole
10 | J2 | 1 | Molex | 436500415 | Digi-Key | WM1919-ND | Connector Header Through Hole 4 position 0.118 (3.00mm)" |  | Through Hole
11 | J3, J4 | 2 | Molex | 436500215 | Digi-Key | WM1917-ND | Connector Header Through Hole 2 position 0.118 (3.00mm)" |  | Through Hole
12 | LED1, LED2 | 2 | Vishay Semiconductor Opto Division | VLMG1300-GS08 | Digi-Key | VLMG1300-GS08CT-ND | LED Indication Green 571nm | 0603 (1608 Metric) | Surface Mount
13 | X1 | 1 |  |  |  |  |  |  |  | DNI
14 | PV1, PV2, PV3, PV4, PV5, PV6, PV7, PV8, PV9 | 9 | Molex | 436500215 | Digi-Key | WM1917-ND | Connector Header Through Hole 2 position 0.118 (3.00mm)" |  | Through Hole
15 | R1, R2 | 2 | Bourns Electronics | 4816P-1-103LF | Digi-Key | 4816P-1-103LFCT-ND | Resistor 10k Ohm ±2% 160mW Power Per Element Isolated 8 Resistor Network/Array | 16-SOIC (0.220, 5.59mm Width)" | Surface Mount
16 | R3 | 1 | Bourns Electronics | 4816P-1-102LF | Digi-Key | 4816P-1-102LFCT-ND | Resistor 1k Ohm ±2% 160mW Power Per Element Isolated 8 Resistor Network/Array | 16-SOIC (0.220, 5.59mm Width)" | Surface Mount
17 | R4, R9, R20, R22, R24, R29, R40, R42, R65 | 9 | Vishay Dale | CRCW12062R20FKEA | Digi-Key | 541-2.20FFCT-ND | Resistor 2.2 Ohms ±1% 0.25W | 1206 (3216 Metric) | Surface Mount
18 | R5, R10, R21, R23, R25, R30, R41, R43, R54, R57, R66 | 11 | Panasonic | ERJPA3F1001V | Digi-Key | P1.0KBYCT-ND | Resistor 1 kOhms ±1% 0.333W | 0603 (1608 Metric) | Surface Mount
19 | R52 | 1 | Vishay | RCS06031K20FKEA | Digi-Key | 541-10435-1-ND | Resistor 1.2 kOhms ±1% 0.25W | 0603 (1608 Metric) | Surface Mount
20 | R53 | 1 | Vishay Dale | RCS0603470RFKEA | Digi-Key | 541-10469-1-ND | Resistor 470 Ohms ±1% 0.25W | 0603 (1608 Metric) | Surface Mount
21 | R55, R56, R58, R59 | 4 | Panasonic | ERJ-PA3F1002V | Digi-Key | P10KBYCT-ND | Resistor 10 kOhms ±1% 0.333W | 0603 (1608 Metric) | Surface Mount
22 | R6, R11, R14, R17, R26, R31, R34, R37, R62 | 9 | Yageo | SR0603FR-7T100KL | Digi-Key | YAG5821CT-ND | Resistor 100 kOhms ±1% 0.25W | 0603 (1608 Metric) | Surface Mount
23 | R7, R12, R15, R18, R27, R32, R35, R38, R63 | 9 | Yageo | SR0603FR-7T2K2L | Digi-Key | YAG5834CT-ND | Resistor 2.2 kOhms ±1% 0.25W | 0603 (1608 Metric) | Surface Mount
24 | R8, R13, R16, R19, R28, R33, R36, R39, R44, R45, R46, R47, R48, R49, R50, R51, R60, R61, R64 | 19 | Vishay | RCS0603120RFKEA | Digi-Key | 541-10426-1-ND | Resistor 120 Ohms ±1% 0.25W | 0603 (1608 Metric) | Surface Mount
25 | S1 | 1 | TE Connectivity | 1-1825059-7 | Digi-Key | 1-1825059-7-ND | SPST Flush Slide Sealed 2.54 mm Pitch Surface Mount DIP Switch |  | Surface Mount
26 | U1, U2, U3, U4, U5, U6, U7, U8, U28, U30 | 10 | Diodes Incorporated | ZXMP7A17GQTA | Digi-Key | ZXMP7A17GQTADICT-ND | MOSFET P-Channel | SOT223 | Surface Mount
27 | U21, U26 | 2 | Texas Instruments | LM324KAPWR | Digi-Key | 296-18449-1-ND | General Purpose Amplifier 4 Circuit | 14-TSSOP (0.173, 4.40mm Width)" | Surface Mount
28 | U9, U10, U11, U12, U13, U14, U15, U16, U17, U18, U19, U20, U22, U23, U24, U25, U27, U29, U31 | 19 | Infineon Technologies | IRLML6244TRPBF | Digi-Key | IRLML6244TRPBFCT-ND | MOSFET N-Channel | Micro3 (SOT-23) | Surface Mount
29 | LED_V1, LED_V2, LED_V3, LED_V4, LED_V5, LED_V6, LED_V7, LED_V8, LED_V9, LED_V10 | 10 | Vishay Semiconductor Opto Division | VLMB1300-GS08 | Digi-Key | VLMB1300-GS08CT-ND | LED Indication Blue 470nm | 0603 (1608 Metric) | Surface Mount
30 | VR1, VR2 | 2 | STMicroelectronics | L78S10CV | Digi-Key | 497-6039-5-ND | Linear Voltage Regulator IC Positive Fixed 1 Output 2A | TO-220 | Through Hole
31 | JP1 | 1 | TE Connectivity AMP Connectors | 1761681-3 | Digi-Key | 1761681-3-ND | Connector Header Through Hole 10 position 0.100 (2.54mm)" |  | Through Hole

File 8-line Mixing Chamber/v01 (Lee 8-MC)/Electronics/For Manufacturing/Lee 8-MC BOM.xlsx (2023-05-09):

Item # | Designator | Qty | Manufacturer | Mfg Part # | Description / Value | Package / Footprint | Type | Instructions / Notes
1 | J9 | 1 | Hirose | FH52-10S-0.5SH | 10 Position FFC, FPC Connector Contacts, Bottom 0.020" (0.50mm) Surface Mount, Right Angle |  | Surface Mount
2 | J1, J2, J3, J4, J5, J6, J7, J8 | 8 | Molex Connector Corporation | 5055670281 | Connector Header Surface Mount, Right Angle 2 position 0.049" (1.25mm) |  | Surface Mount

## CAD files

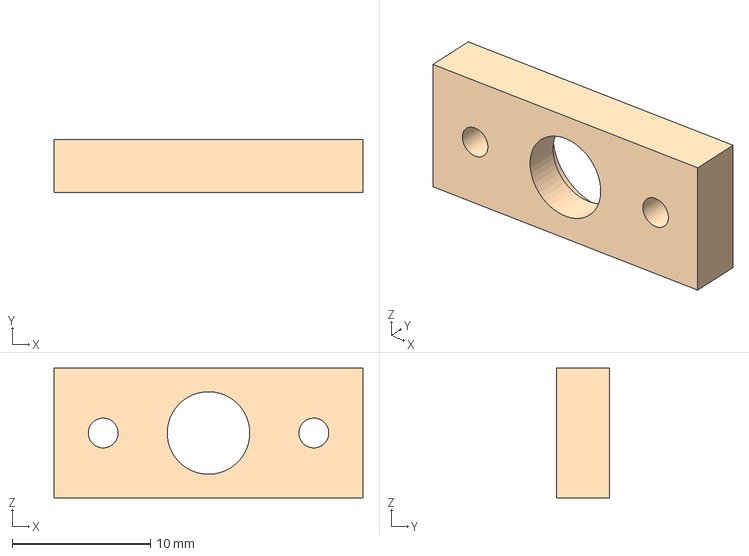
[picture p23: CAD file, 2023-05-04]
8-line Olfactometer/Hardware/For Manufacturing/CAD files/main_manifold_cover_1v_v02.stp
22.4 x 3.81 x 9.40 mm

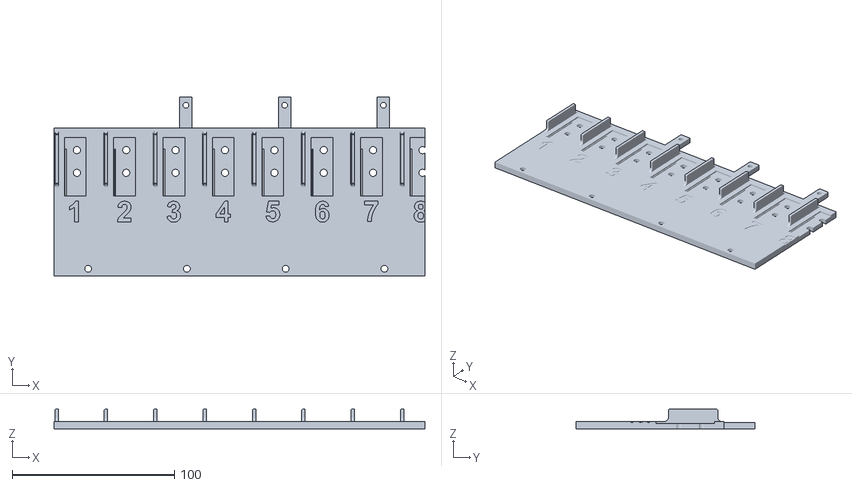
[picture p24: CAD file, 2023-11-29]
8-line Olfactometer/3D printed parts/mainPlate.stl
229.0 x 110.5 x 12.2

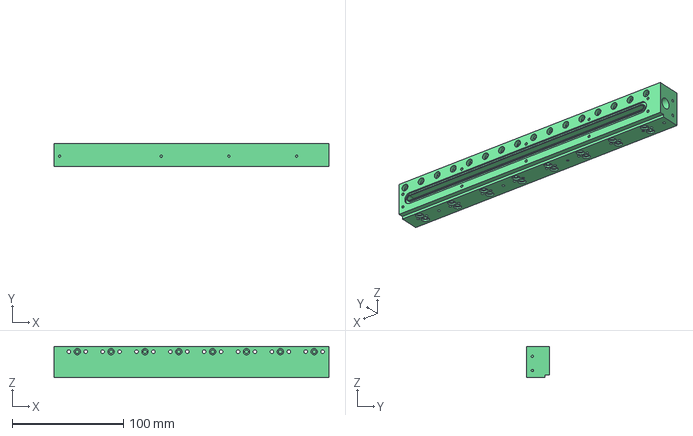
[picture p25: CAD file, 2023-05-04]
8-line Olfactometer/Hardware/For Manufacturing/CAD files/main_manifold_8v_v02.stp
247.6 x 20.3 x 27.9 mm

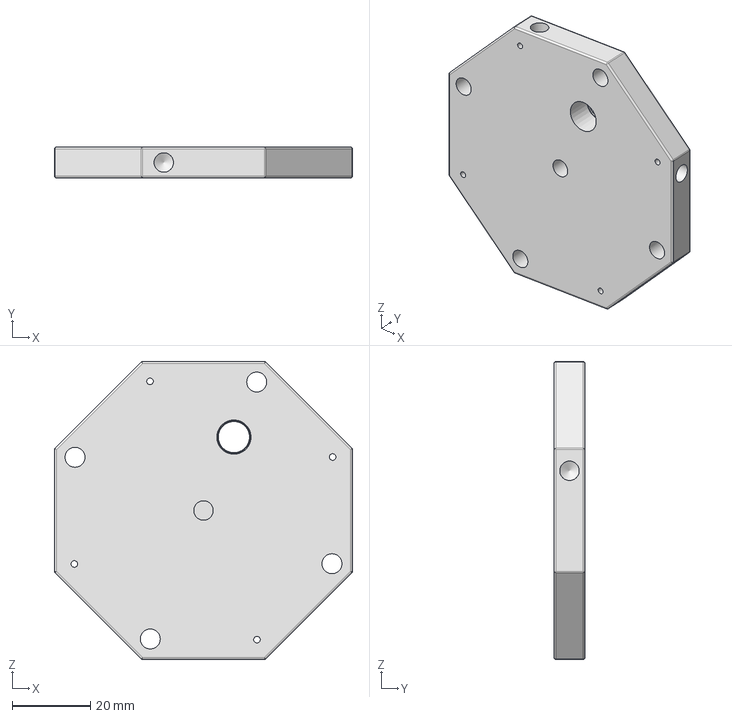
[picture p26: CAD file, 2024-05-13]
8-line Mixing Chamber/For Manufacturing (Hardware)/CAD files/Clippard 8-MC cover v2A.stp
76.2 x 7.94 x 76.2 mm

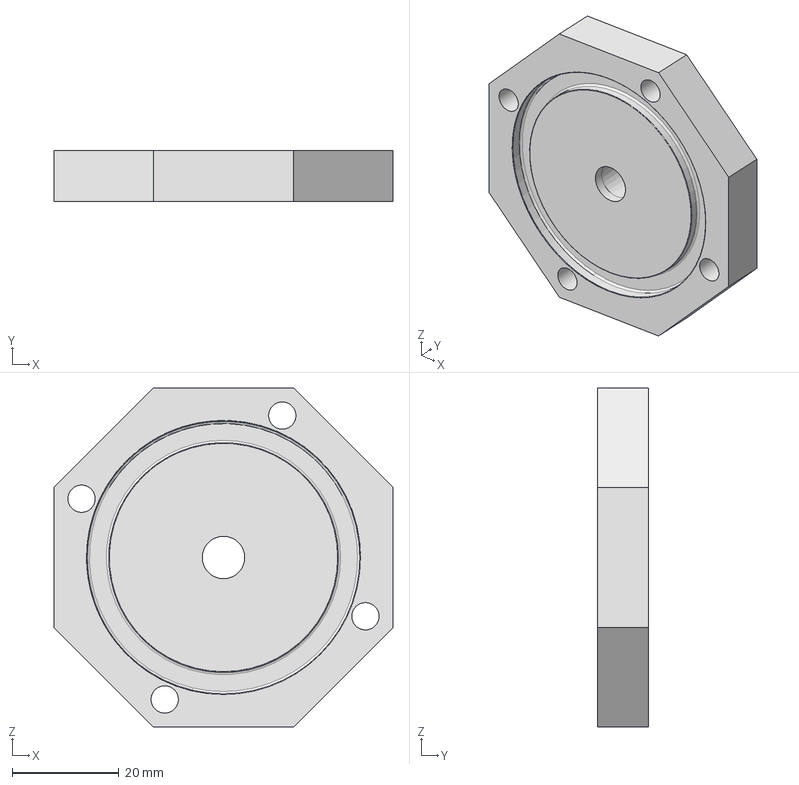
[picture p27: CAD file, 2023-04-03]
8-line Mixing Chamber/v01 (Lee 8-MC)/Hardware/Lee 8-MC cover_v01.stp
63.5 x 9.52 x 63.5 mm

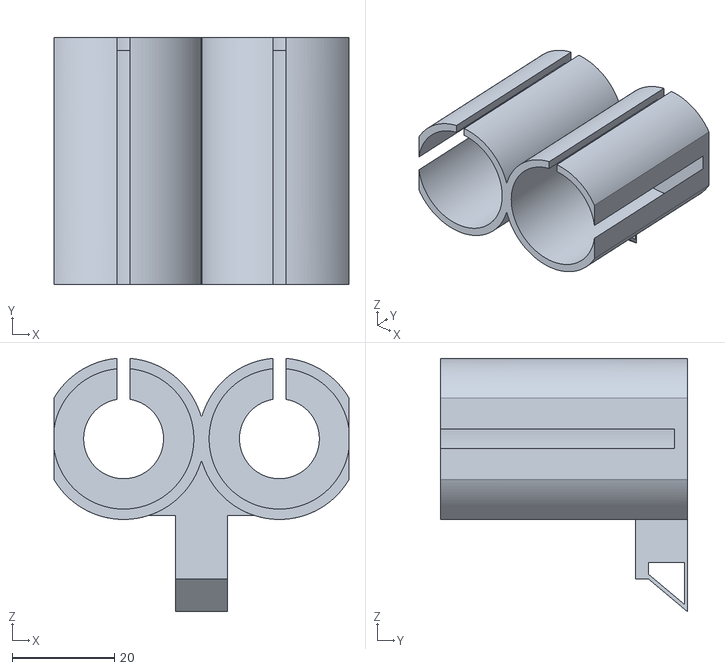
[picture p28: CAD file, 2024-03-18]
8-line Olfactometer/3D printed parts/vialHolder_2v.stl
57.7 x 48.3 x 49.5

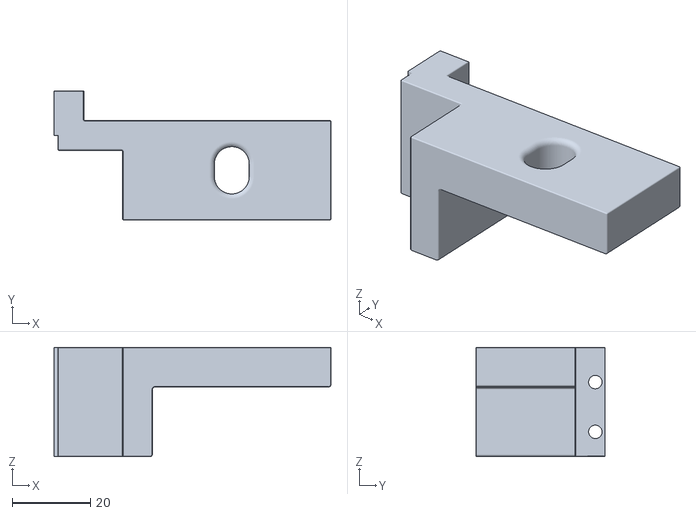
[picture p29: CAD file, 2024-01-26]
8-line Olfactometer/Hardware/3D printed parts/for mounting/mount_right.stl
70.7 x 33.0 x 27.9

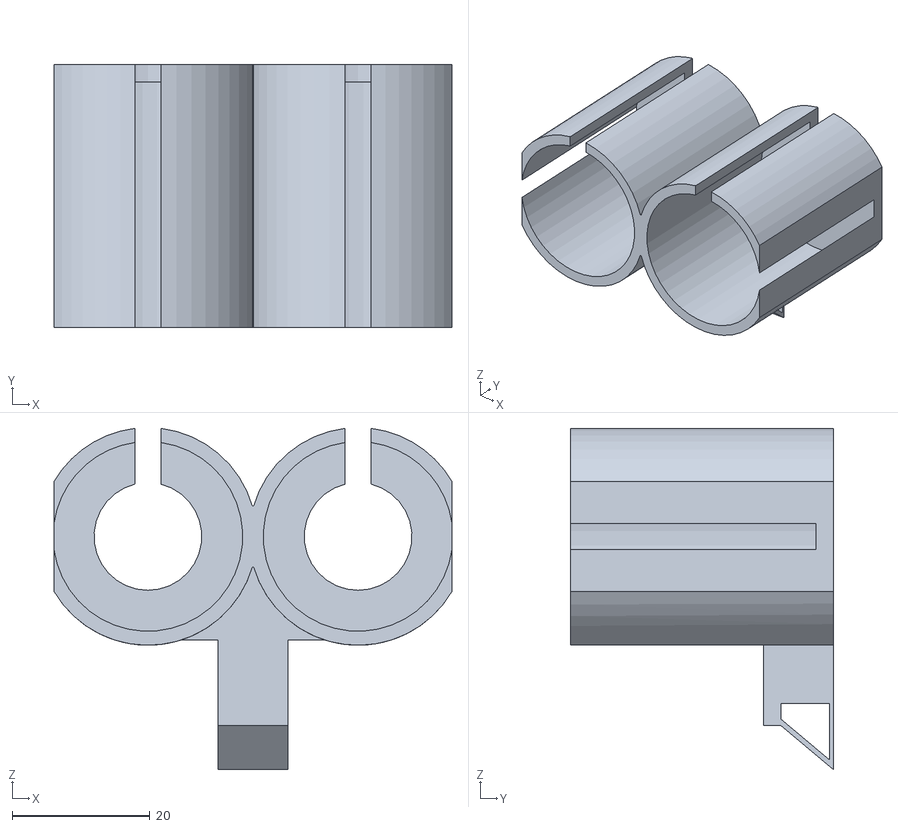
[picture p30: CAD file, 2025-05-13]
8-line Olfactometer/Hardware/3D printed parts/vialHolder_2v_02.stl
57.7 x 38.1 x 49.5

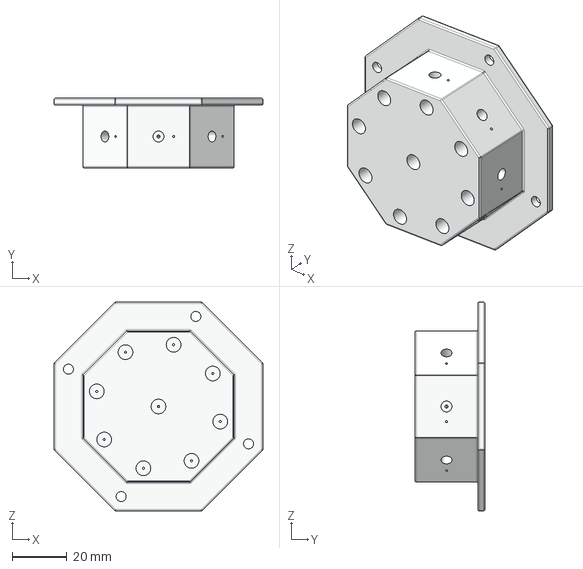
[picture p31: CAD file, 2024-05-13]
8-line Mixing Chamber/For Manufacturing (Hardware)/CAD files/Clippard 8-MC heart v2A.stp
76.2 x 25.4 x 76.2 mm

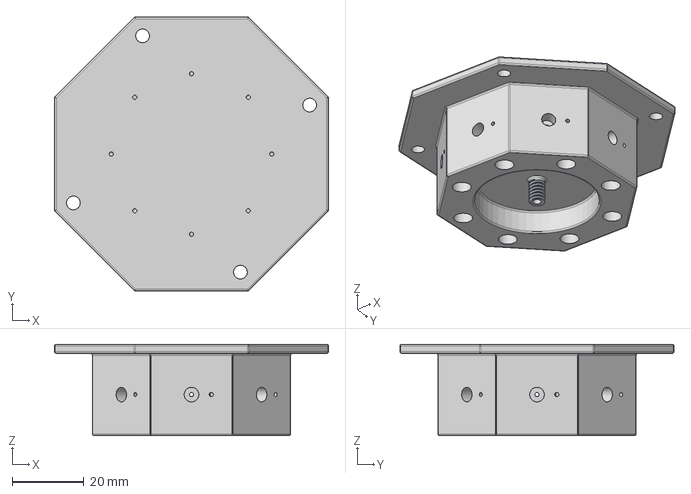
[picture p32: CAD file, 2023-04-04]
8-line Mixing Chamber/For Manufacturing (Hardware)/Clippard 8-MC v01/CAD files/Clippard 8-MC heart_v01.step
76.2 x 76.2 x 25.4 mm

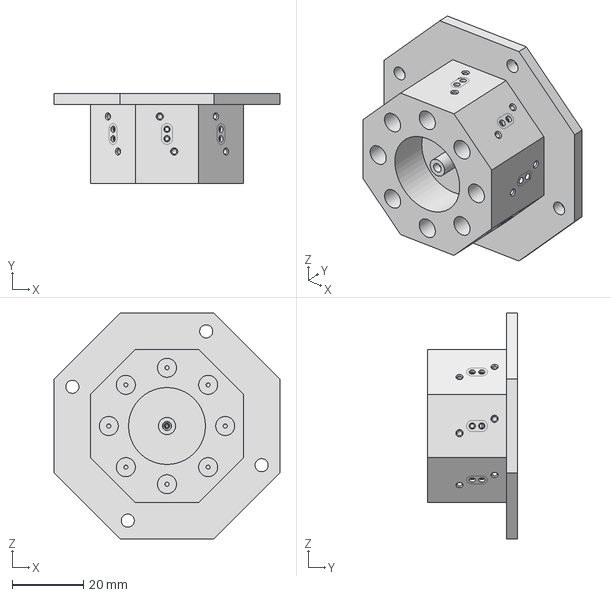
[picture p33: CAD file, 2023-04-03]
8-line Mixing Chamber/v01 (Lee 8-MC)/Hardware/Lee 8-MC heart_v01.stp
63.5 x 25.4 x 63.5 mm

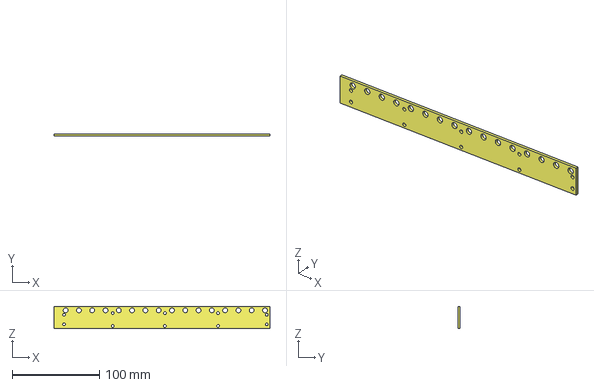
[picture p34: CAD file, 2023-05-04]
8-line Olfactometer/Hardware/For Manufacturing/CAD files/top_cover_02.stp
247.6 x 2.54 x 25.8 mm

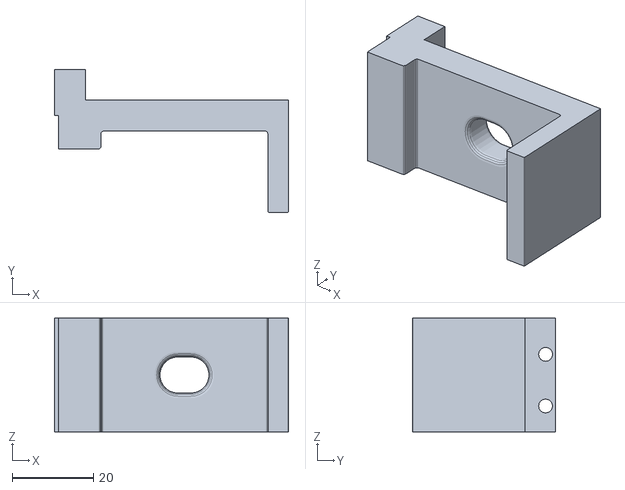
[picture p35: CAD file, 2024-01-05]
8-line Olfactometer/Hardware/3D printed parts/for mounting/mount_bracket item_8_withhole.stl
57.5 x 35.1 x 27.9

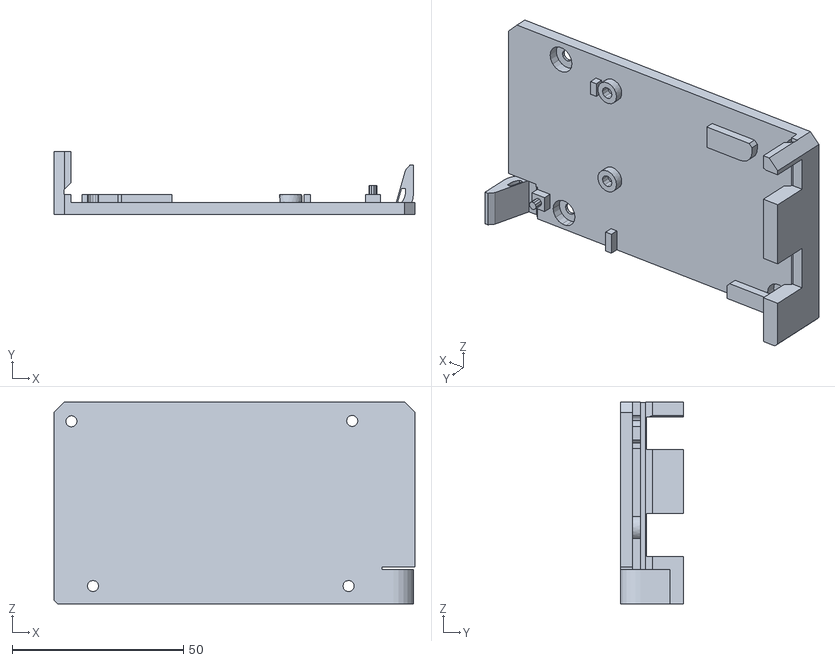
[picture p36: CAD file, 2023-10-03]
8-line Olfactometer/Hardware/3D printed parts/Arduino_holder.stl
105.5 x 18.4 x 58.9

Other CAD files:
8-line Mixing Chamber/For Manufacturing (Hardware)/Clippard 8-MC v01/CAD files/Clippard 8-MC cover_v01.step
8-line Olfactometer/Hardware/3D printed parts/for mounting/mount_left.stl
8-line Mixing Chamber/Electronics/3D PCB/3D PCB Components/1-copper.ipt
8-line Mixing Chamber/Electronics/3D PCB/3D PCB Components/1-soldermask.ipt
8-line Mixing Chamber/Electronics/3D PCB/3D PCB Components/16-copper.ipt
8-line Mixing Chamber/Electronics/3D PCB/3D PCB Components/16-soldermask.ipt
8-line Mixing Chamber/Electronics/3D PCB/3D PCB Components/1761681-3 v1.ipt
8-line Mixing Chamber/Electronics/3D PCB/3D PCB Components/436500215_PART1_Tin.ipt
8-line Mixing Chamber/Electronics/3D PCB/3D PCB Components/436500215_PART2_Tin.ipt
8-line Mixing Chamber/Electronics/3D PCB/3D PCB Components/436500215_Tin v3.iam
8-line Mixing Chamber/Electronics/3D PCB/3D PCB Components/436500215_Tin v3_1.iam
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

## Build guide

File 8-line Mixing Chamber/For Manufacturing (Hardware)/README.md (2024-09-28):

## Clippard 8-MC heart (v2A) inner tubing dimensions

1/32" ID where NResearch fittings connect (odor in, exhaust)  
3/64" ID for the rest of it (clean air in, valve outlet)  

<br>
<br>

## Drawing files

**Clippard 8-MC cover v2A.dwg**  
**Clippard 8-MC heart v2A.dwg**  
^^ files that  were sent for manufacturing (Xometry)  
<br>

**Clippard 8-MC cover v2A_full.dwg**  
**Clippard 8-MC heart v2A_full.dwg**  
^^ created by me (later) for my own reference

<br>
<br>

## Changes from v1 to v2:

### Clippard 8-MC heart:
- Odor input hole (from the bottom) was previously not aligned with its connecting inlet hole (horizontal) - tied geometries together  
	- (x_Clippard 8-MC heart v50 v3 shows the initial error)  
	- (Clippard 8-MC heart_v01 has some fixed things in it)  
- Odor (vial) inlet ID changed from .046" to .03125" (1/32") (to match 1/32" ID tubing)  

### Clippard 8-MC cover:
- PCB mounting holes: just picked a dimension since it seems last time it was made up  

<br>
<br>

## Manufacturing details

04/11/2024  
Clippard 8-MC v2A

**Material:** Stainless Steel 303  
**Surface Roughness:** 125uin/3.2um Ra

<br>
<br>

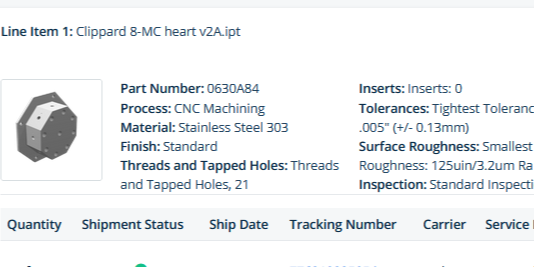
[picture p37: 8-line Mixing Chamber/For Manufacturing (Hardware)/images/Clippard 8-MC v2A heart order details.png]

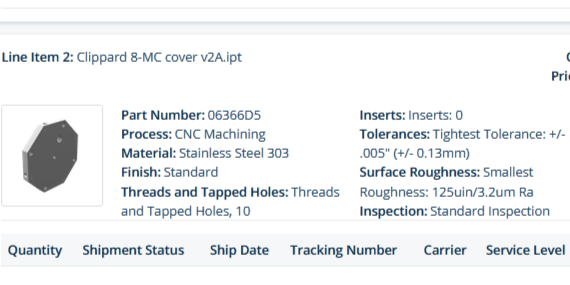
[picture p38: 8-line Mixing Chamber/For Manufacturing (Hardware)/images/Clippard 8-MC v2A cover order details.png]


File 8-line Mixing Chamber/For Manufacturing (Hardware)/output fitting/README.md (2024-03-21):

## Nut for Precision Compression Fitting 10-24

#### Custom version of McMaster-Carr [Nut for 1/16" Tube OD Precision Compression Fitting for Stainless Steel Tubing](https://www1.mcmaster.com/8239K216/) 8239K216

<br>

The outlet thread on Clippard 8-MC heart_v01 was machined as a #10-24 thread. Therefore, the intended fitting (McMaster-Carr 8239K216, which has a #10-32 thread), was not compatible.

A custom nut was manufactured to fit onto the Clippard heart. The nut is identical to the McMaster-Carr part, with the exception of the thread pitch (changed to #10-24).

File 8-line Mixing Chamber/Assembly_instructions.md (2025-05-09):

## Connect cover to heart

- (x1) Clippard 8-MC cover
- (x1) Clippard 8-MC heart
- (x4) 10-24 x 1/2" screw
- (x1) #227 O-ring
- (x1) 1/8 NPT Male to 1/4" Tube OD Push-To-Connect Fitting

<br>
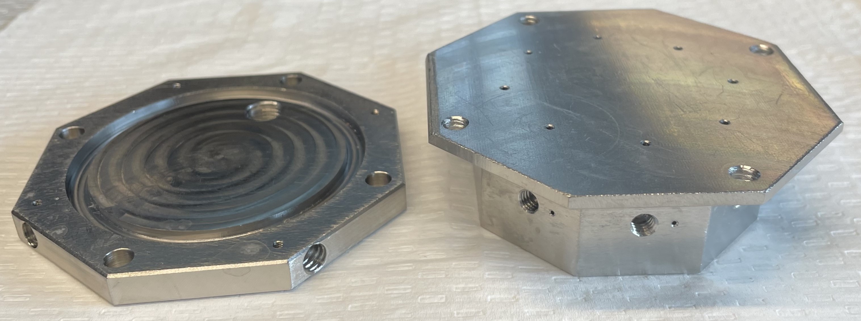
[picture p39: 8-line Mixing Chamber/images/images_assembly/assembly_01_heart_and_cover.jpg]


Fit o-ring into cover.  

Place cover on top of heart. Secure with 10-24 screws. (May be easiest to hold assembly upside-down.) Tighten screws only a little bit at a time, and in random order. (This will ensure o-ring stays in correct position.)  
<p align="center">
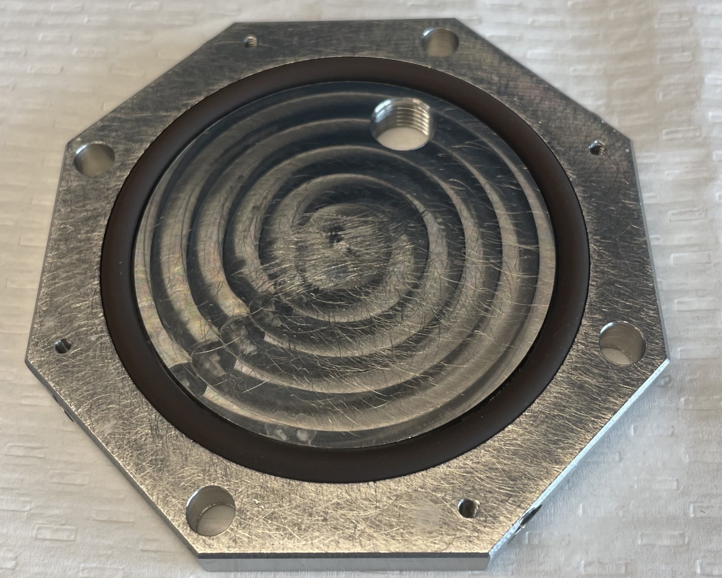
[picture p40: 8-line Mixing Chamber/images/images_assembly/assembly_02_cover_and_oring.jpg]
    
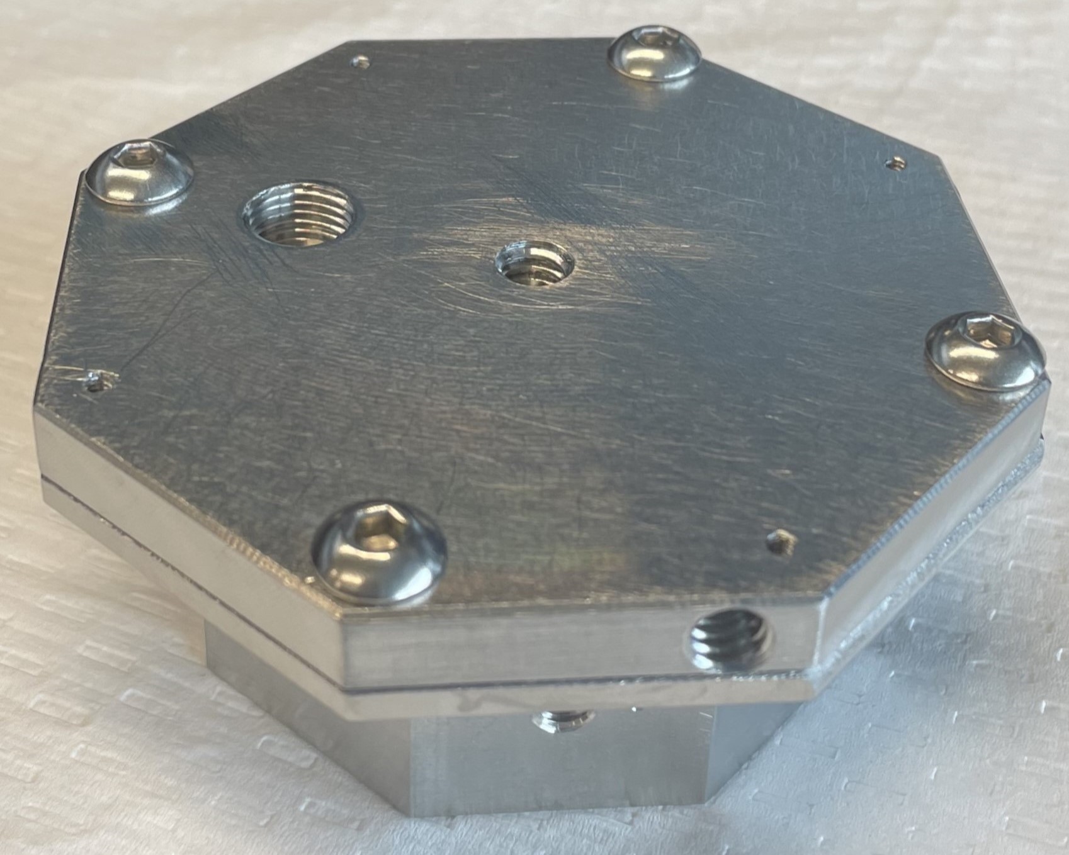
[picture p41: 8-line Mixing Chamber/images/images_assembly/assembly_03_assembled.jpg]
    
</p>

Screw input fitting into cover.  
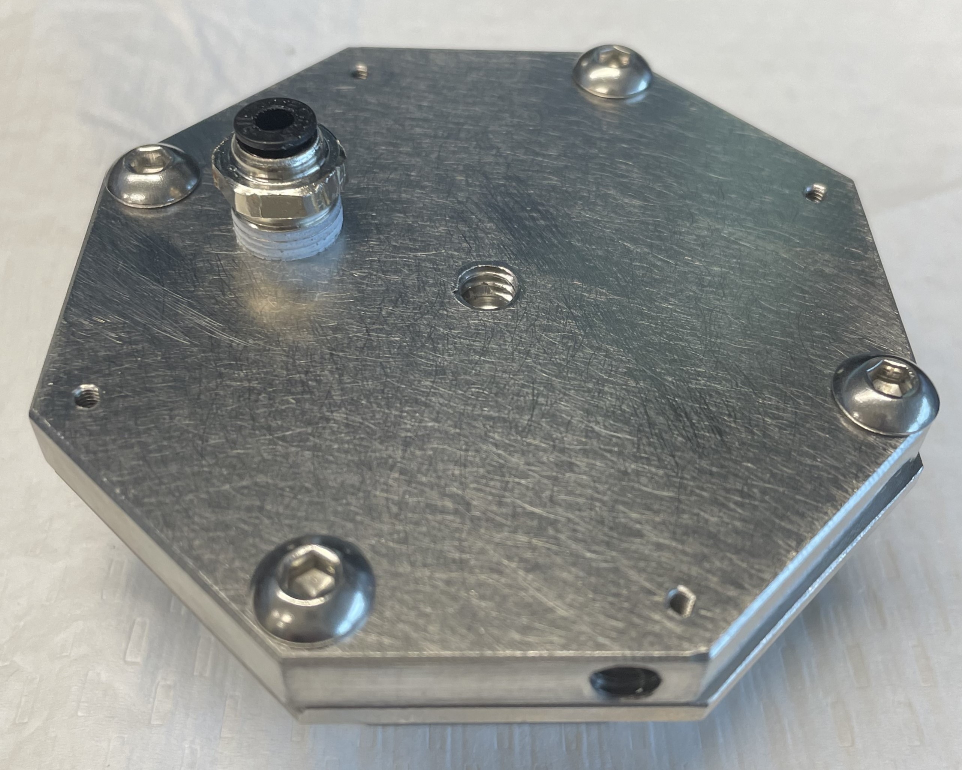
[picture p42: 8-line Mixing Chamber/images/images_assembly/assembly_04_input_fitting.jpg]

<br>

## PCB to cover

- (x1) PCB
- (x4) Nylon Unthreaded Spacer
- (x4) 2-56 x 1/4" Nylon Pan Head Screw

Place spacers on cover, on top of the holes with the small screw threads.  
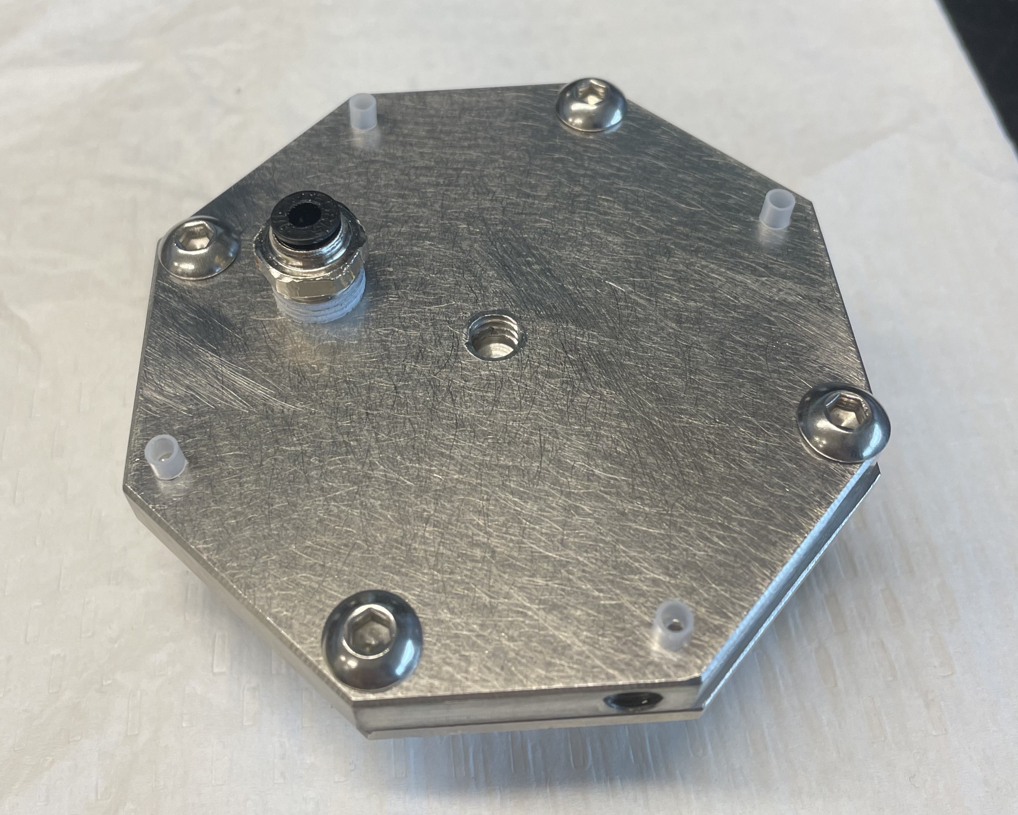
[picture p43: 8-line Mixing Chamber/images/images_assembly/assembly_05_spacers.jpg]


Insert screws through holes in PCB.  
Carefully place the PCB on top of the spacers, positioning it so that the screws pass through the spacers.  
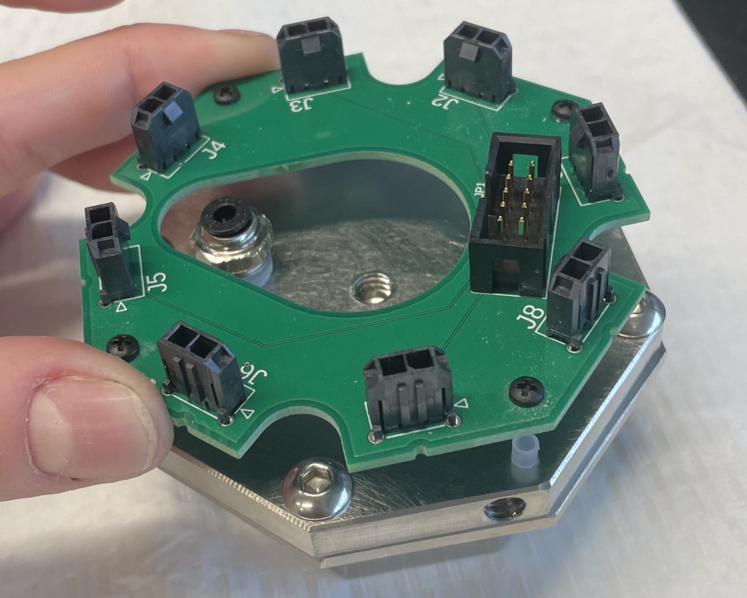
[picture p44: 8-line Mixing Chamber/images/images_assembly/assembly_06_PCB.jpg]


Screw them into the cover to secure the PCB.  
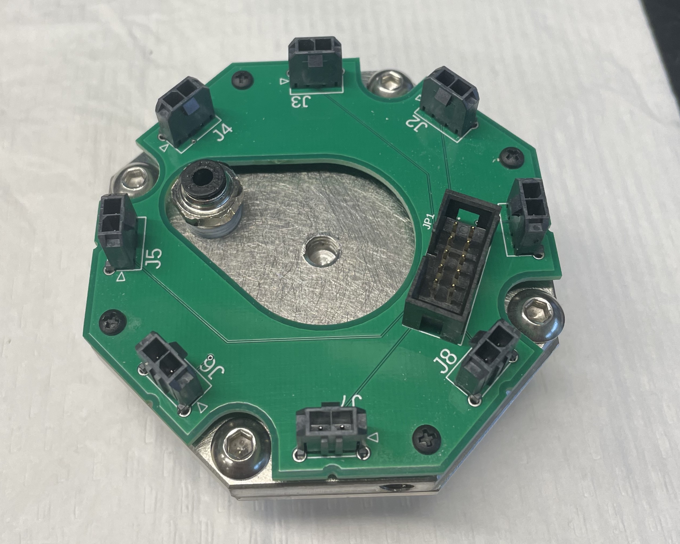
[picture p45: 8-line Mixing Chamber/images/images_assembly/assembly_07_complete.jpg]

<br>

## mount it

<br>
- However you plan on mounting it

<br><br>

## isolation valves
 - (x8) Clippard EV-2M-24-H-V isolation valves

 <br>
 - Screw in until hand tight, then use something to get them an extra 1/4 turn or so. Connect to PCB.
<br><br>

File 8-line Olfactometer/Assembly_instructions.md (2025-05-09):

## Main manifold to top cover (with o-ring)

- (x1) main manifold
- (x1) top cover
- (x1) o-ring (-051)
- (x10) 4-40 x 1/4" screw
- (x10) 4-40 washer
- (x1) Straight Adapter, for 1/4" Tube OD x 1/8 NPT Male

<br>
Fit o-ring into main manifold groove.

<br>
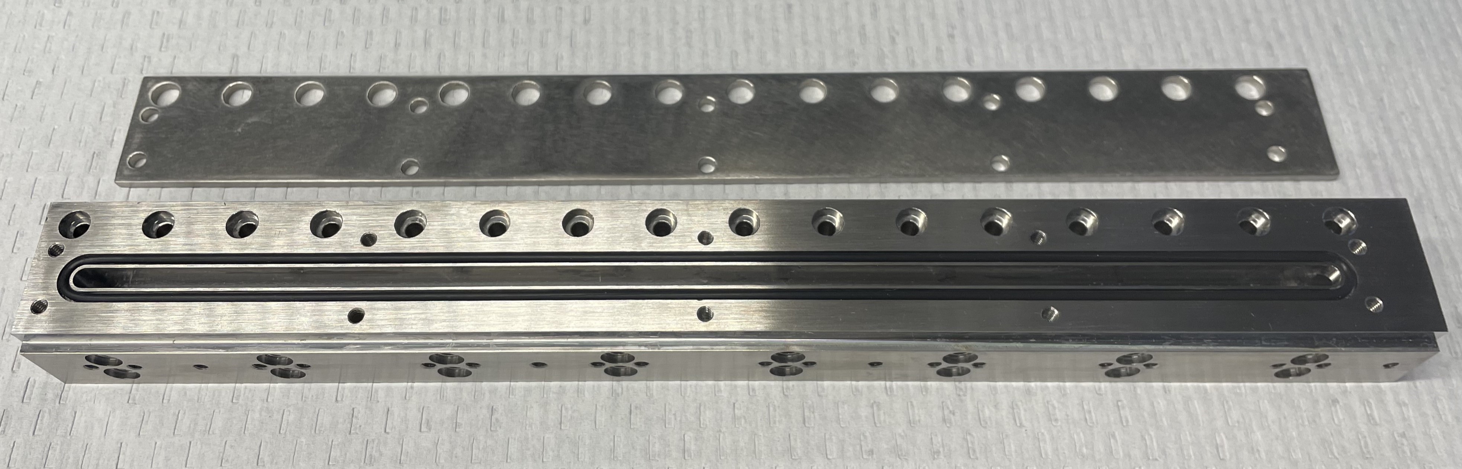
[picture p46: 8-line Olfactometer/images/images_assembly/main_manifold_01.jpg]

Place top cover on top of main manifold. Secure with 4-40 screws & washers.  

<br>
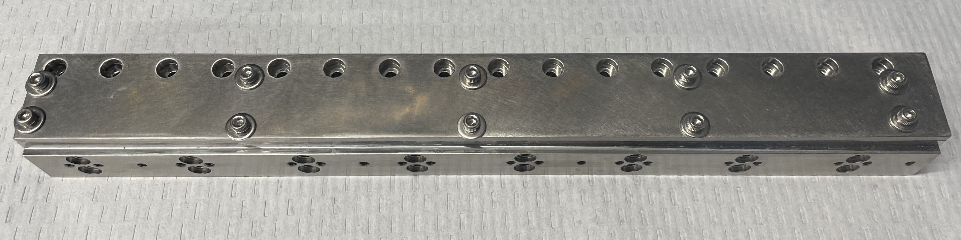
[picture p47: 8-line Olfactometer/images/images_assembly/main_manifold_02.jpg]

Screw input fitting into main manifold.

<br>
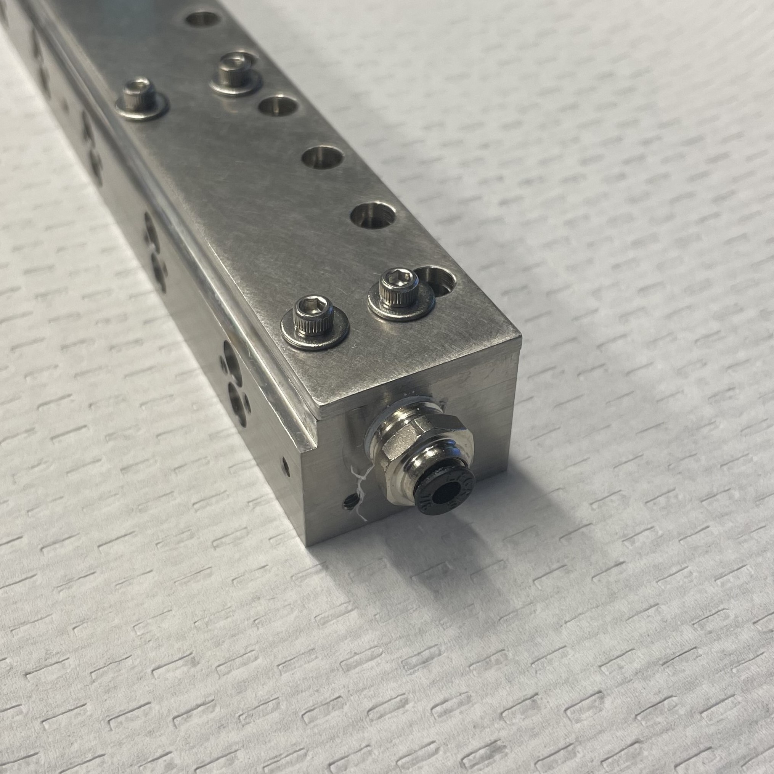
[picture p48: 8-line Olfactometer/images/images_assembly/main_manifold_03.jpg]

<br>

## Proportional valves to main manifold

- (x8) proportional valves
- (x16) o-rings
- (x16) 4-40 x 5/8" screw

Place one o-ring onto each countersink of the proportional valve. Insert screws through holes on opposite side of valve. Hold valve flush to main manifold and tighten the screws to secure.  
<br>

## Main plate

- (x1) main plate
- (x3) 4-40 x 1/4" screw

Attach main plate to main manifold using 4-40 x 1/4" screws.  
<br>

## Flow sensors

### Output tubing
- (x8) flow sensors
- 1/4" OD 1/8" ID tubing
- (x8) male luer to 1/8" barb

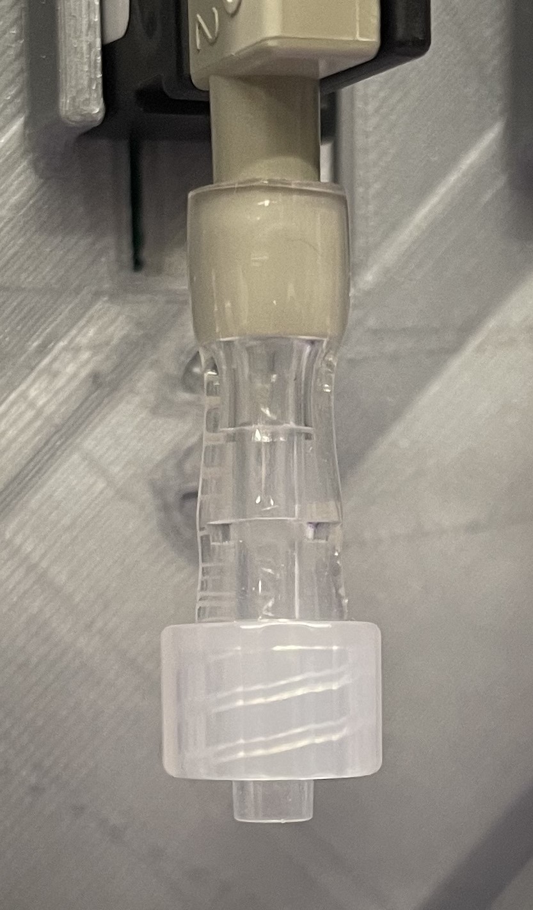
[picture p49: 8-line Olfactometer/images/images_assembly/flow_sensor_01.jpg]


Cut a ~1" piece of tubing. Slide the end onto the output (P2) of the flow sensor. Insert the luer barb into the other end of the tubing.  
<br>

### Input Connection
- (x8) o-rings
- (x8) main manifold cover
- (x16) 4-40 x 7/8" screw

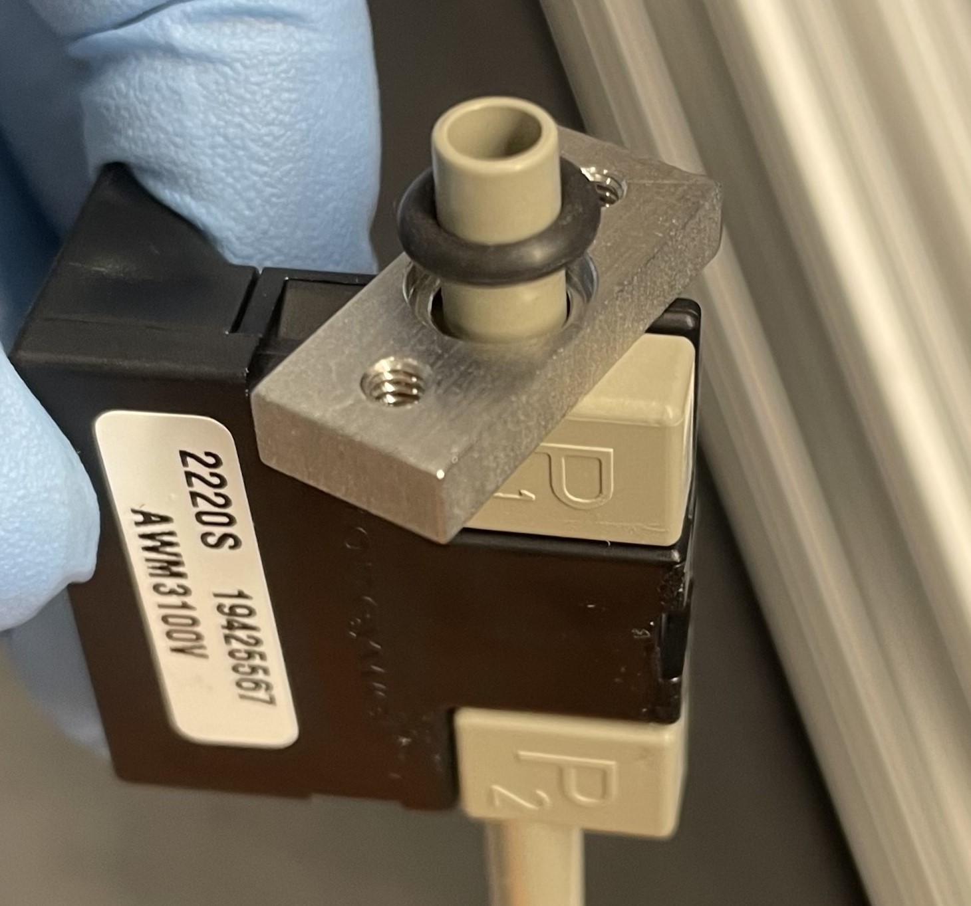
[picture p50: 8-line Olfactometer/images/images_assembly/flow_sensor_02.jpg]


Insert flow sensor input (P1) through the main manifold cover (with the o-ring groove facing away from the flow sensor). Slide o-ring onto the end of the flow sensor (same side as the o-ring groove).  
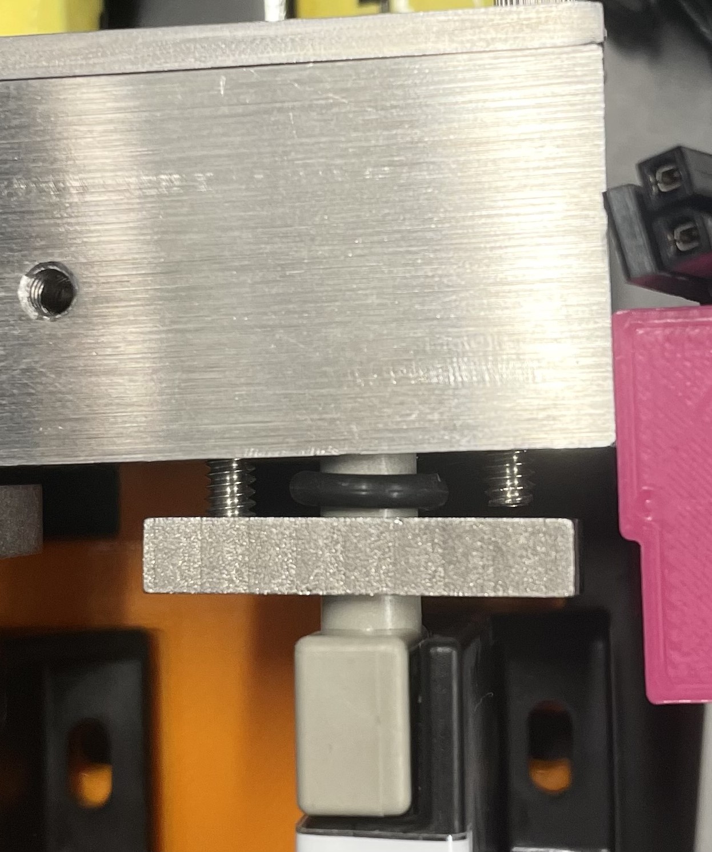
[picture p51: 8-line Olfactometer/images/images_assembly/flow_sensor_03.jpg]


Drop (x2) 4-40 x 7/8" screws through the top of hte main manifold. Fit the flow sensor input into the main manifold (header pins should slide through the slot in the main plate).  

While securely holding the input (P1) of the flow sensor flush to the main manifold, secure the screws into the main manifold cover.  
<br>

### Secure to main plate

- (x8) 4-40 x 3/8" screws
- (x8) 4-40 hex nuts

Secure flow sensors to main plate using 4-40 x 3/8" screws and hex nuts. (possibly connect PCB before doing so, to make sure it's all aligned) (They don't need to be super tight, just secure enough to the main plate to make it easier to connect the PCB).  
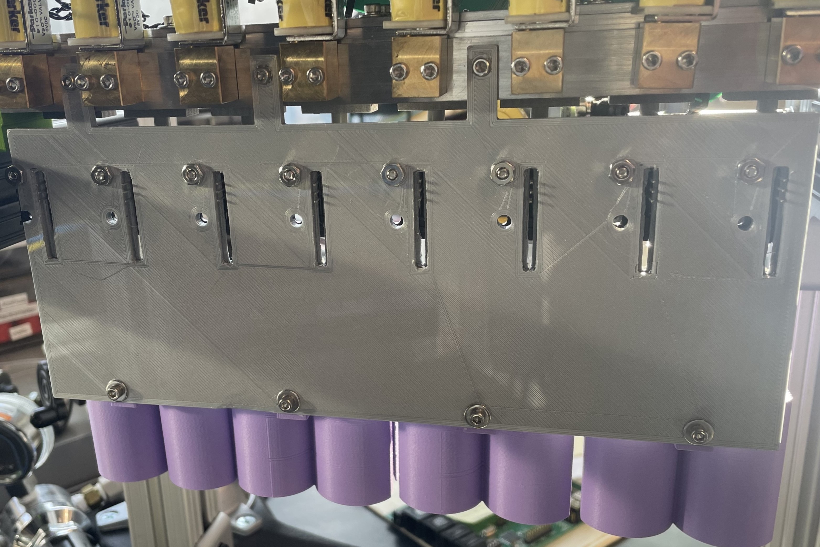
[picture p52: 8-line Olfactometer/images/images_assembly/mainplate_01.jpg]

<br>

## Mounting brackets

- (x2) mounting brackets
- (x4) 4-40 x 1/2" screw
- (x2) M8 screws

Attach mounting brackets to main manifold using 4-40 screws.  
Use M8 screws to mount main manifold (for convenience for rest of assembly).  
<br>

## Vial holders

- (x4) vial holders
- (x4) 4-40 heat set inserts
- (x4) 4-40 x 3/8" screws

Install heat set inserts into vial holders.  
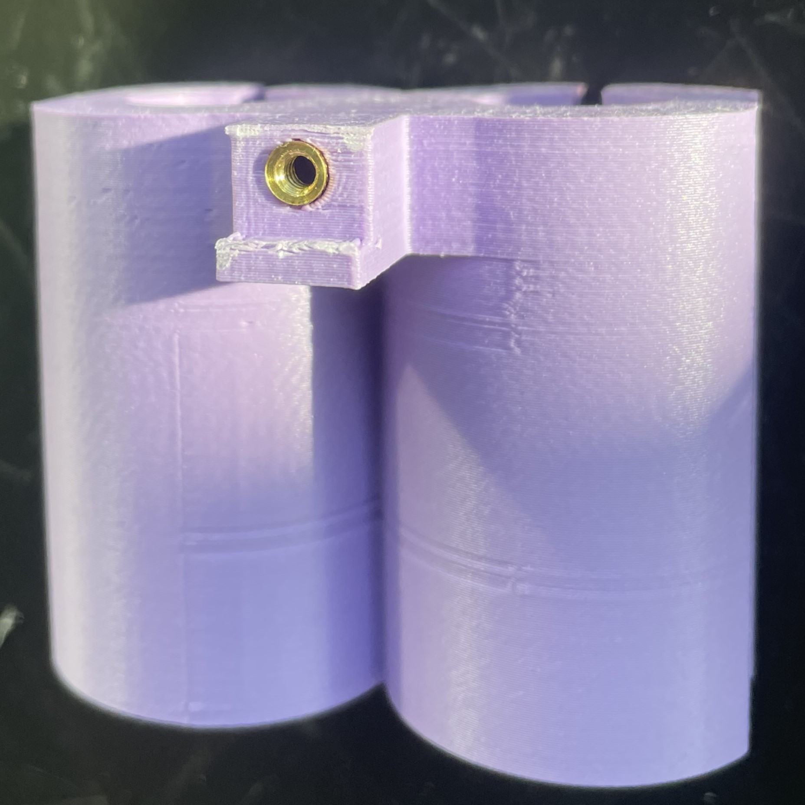
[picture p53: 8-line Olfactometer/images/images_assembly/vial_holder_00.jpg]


Position vial holder flush against main plate and secure with screws.  
<p align="center">
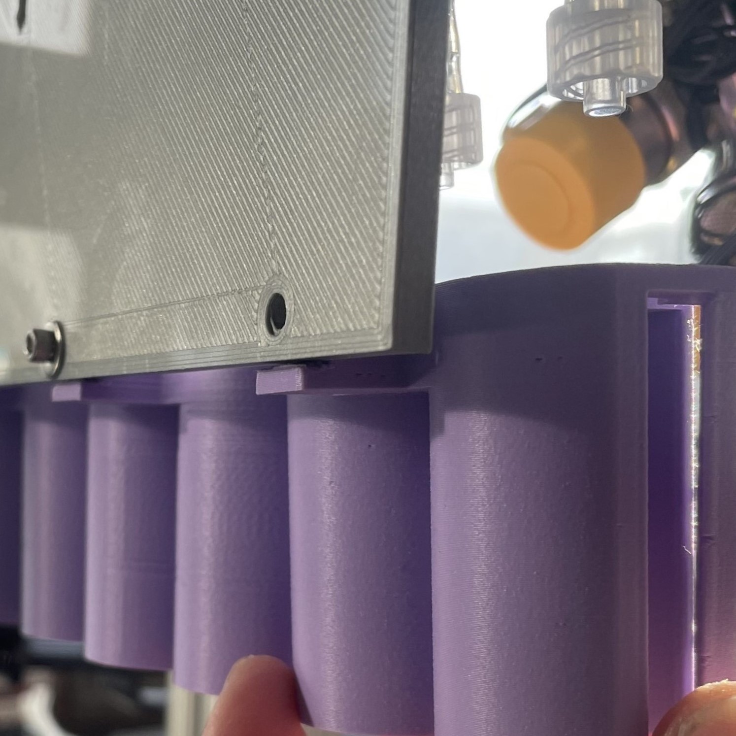
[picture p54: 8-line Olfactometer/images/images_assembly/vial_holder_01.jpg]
    
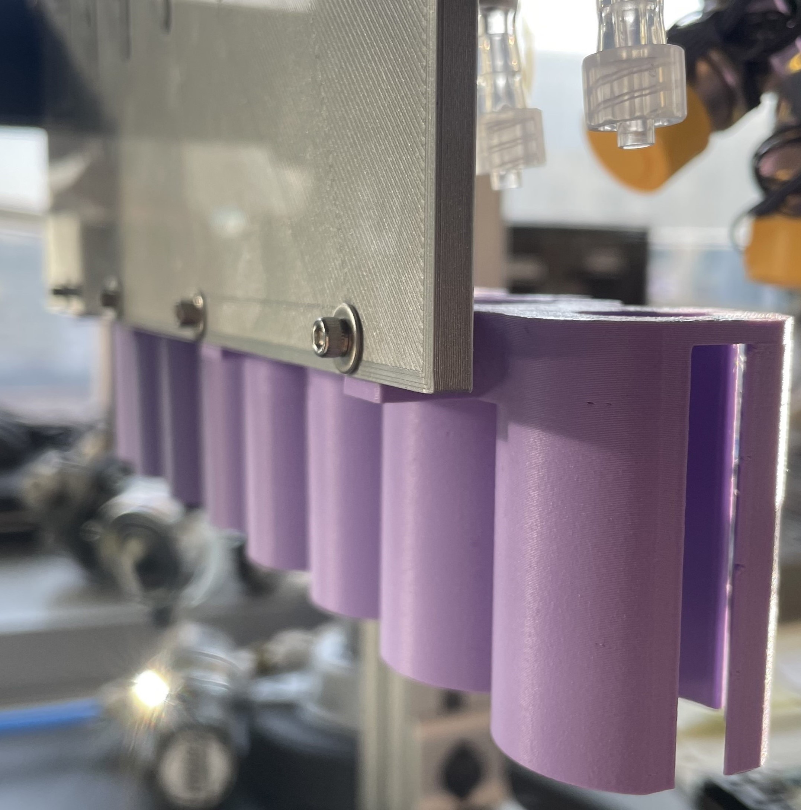
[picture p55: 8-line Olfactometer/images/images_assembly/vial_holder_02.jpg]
    
</p>
<br>

## PCB

Align flow sensor headers on PCB with flow sensor pins.
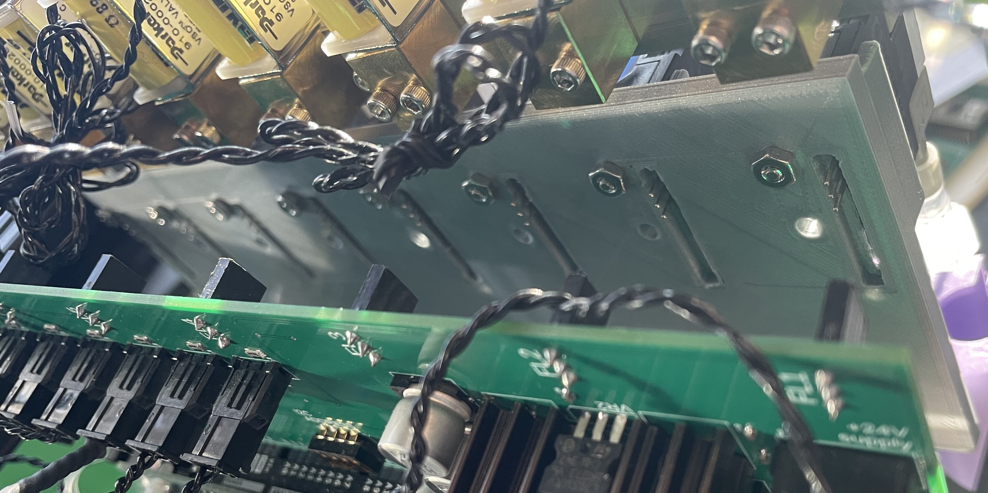
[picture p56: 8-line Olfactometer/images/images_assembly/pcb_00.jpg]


Carefully slide PCB onto flow sensors.  
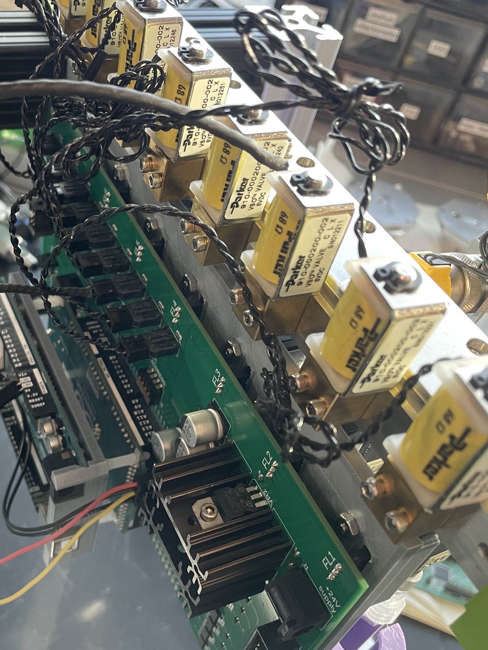
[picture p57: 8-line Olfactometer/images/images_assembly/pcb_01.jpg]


Make sure that all flow sensor pins are in the correct spot. (If any of the pins are out of place, flow sensors will burn out).  
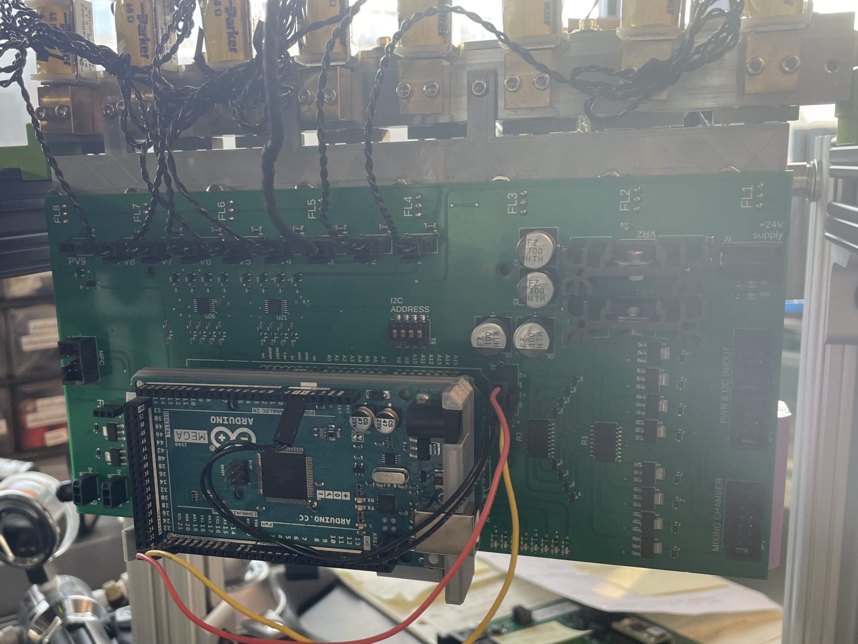
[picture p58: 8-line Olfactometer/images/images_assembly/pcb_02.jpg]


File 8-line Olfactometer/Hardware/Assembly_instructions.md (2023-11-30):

## main manifold to top cover (with o-ring)

- (x1) Straight Adapter, for 1/4" Tube OD x 1/8 NPT Male
- (x1) main manifold
- (x1) top cover
- (x1) o-ring
- (x10) 4-40 x 1/4" screw
- (x10) 4-40 washer

<br>
Screw input fitting into main manifold.
<br>
Fit o-ring into main manifold groove. Place top cover on top of main manifold. Secure with screws & washers.

<br><br>

## proportional valves to main manifold

- (x8) proportional valves
- (x16) o-rings
- (x16) 4-40 x 5/8" screw

<br>
Connect proportional valves to main manifold.

<br><br>

## main plate

- (x1) main plate
- (x3) 4-40 x 1/4" screw

<br>
Attach main plate to main manifold using 4-40 x 1/4" screws.

<br><br>

## flow sensors

- (x8) flow sensors
- 1/4" OD 1/8" ID tubing
- (x8) male luer to 1/8" barb

<br>
Cut a ~1" piece of tubing. Slide the end onto the output (P2) of the flow sensor. Insert the luer barb into the other end of the tubing.
<br>
<br><br>

- (x8) o-rings
- (x16) 4-40 x 7/8" screw
- (x8) 4-40 x 3/8" screws, (x8) 4-40 hex nuts

<br>
Insert flow sensor input (P1) through the main manifold cover (with the o-ring groove facing away from the flow sensor). Slide o-ring onto the end of the flow sensor (same side as the o-ring groove).
<br><br>
Drop (x2) 4-40 x 7/8" screws through the main manifold. Fit the flow sensor input into the main manifold (header pins should slide through the slot in the main plate).
<br><br>
While securely holding the input (P1) of the flow sensor flush to the main manifold, secure the screws into the main manifold cover.
<br><br><br>
Secure flow sensors to main plate using 4-40 x 3/8" screws and hex nuts. (possibly connect PCB before doing so, to make sure it's all aligned)

<br><br>

## mounting brackets

- (x2) mounting brackets
- (x4) 4-40 x 1/2" screw
- (x2) M8 screws

<br>
Attach mounting brackets to main manifold using 4-40 screws.
<br>
Use M8 screws to mount main manifold (for convenience for rest of assembly)

<br><br>

## vial holders

- (x4) vial holders
- (x4) 4-40 heat set inserts
- (x4) 4-40 x 3/8" screws

<br>
Install heat inserts into vial holders.
<br><br>
Secure vial holders to main plate with screws.

<br><br>

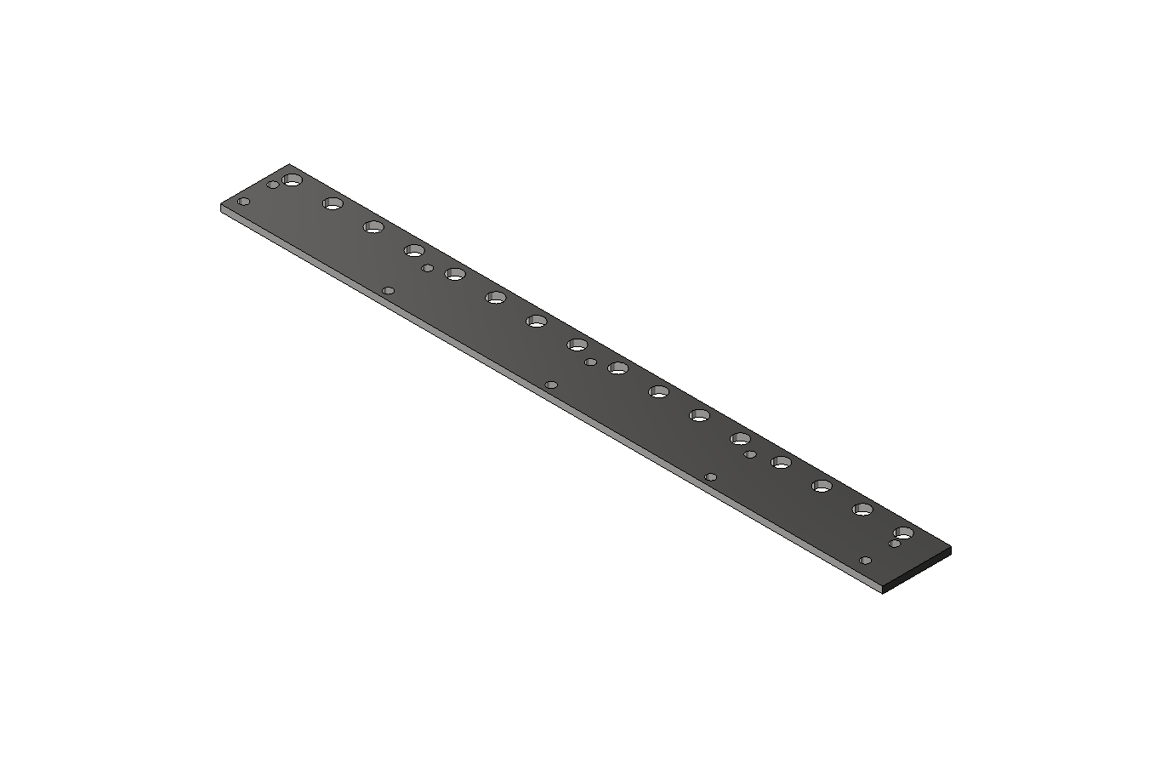
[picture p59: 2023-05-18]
8-line Olfactometer/Hardware/For Manufacturing/images/top_cover_02.png

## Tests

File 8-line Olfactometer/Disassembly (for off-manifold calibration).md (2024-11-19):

# Olfactometer disassembly (draft)

- Disconnect input air (Alicat MFC) from olfactometer manifold
- Disconnect 24V power supply & Arduino cable from olfactometer PCB
- Disconnect Mixing Chamber cable from olfactometer PCB
- Carefully remove olfactometer PCB from flow sensors

<br>

**To remove single flow sensor:**  

- Disconnect flow sensor output luer fitting from needle in odor vial.  
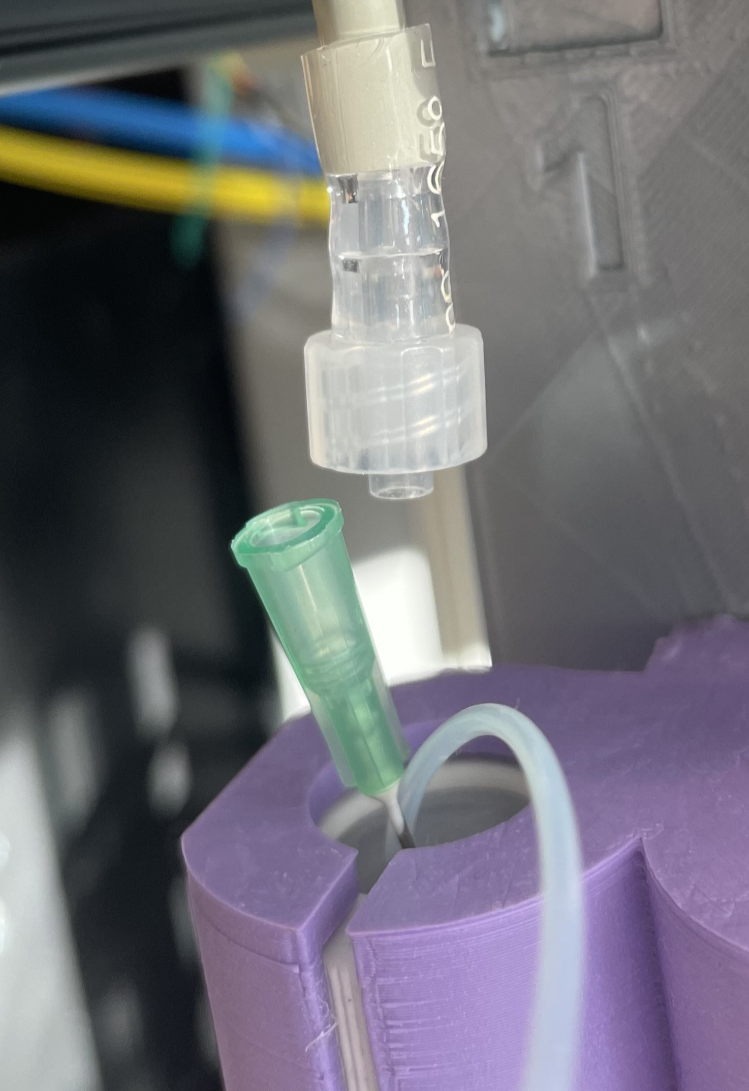
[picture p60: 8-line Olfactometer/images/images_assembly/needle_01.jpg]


- Remove 4-40 screw and nut securing flow sensor to 3D printed main plate.  
<p align="center">
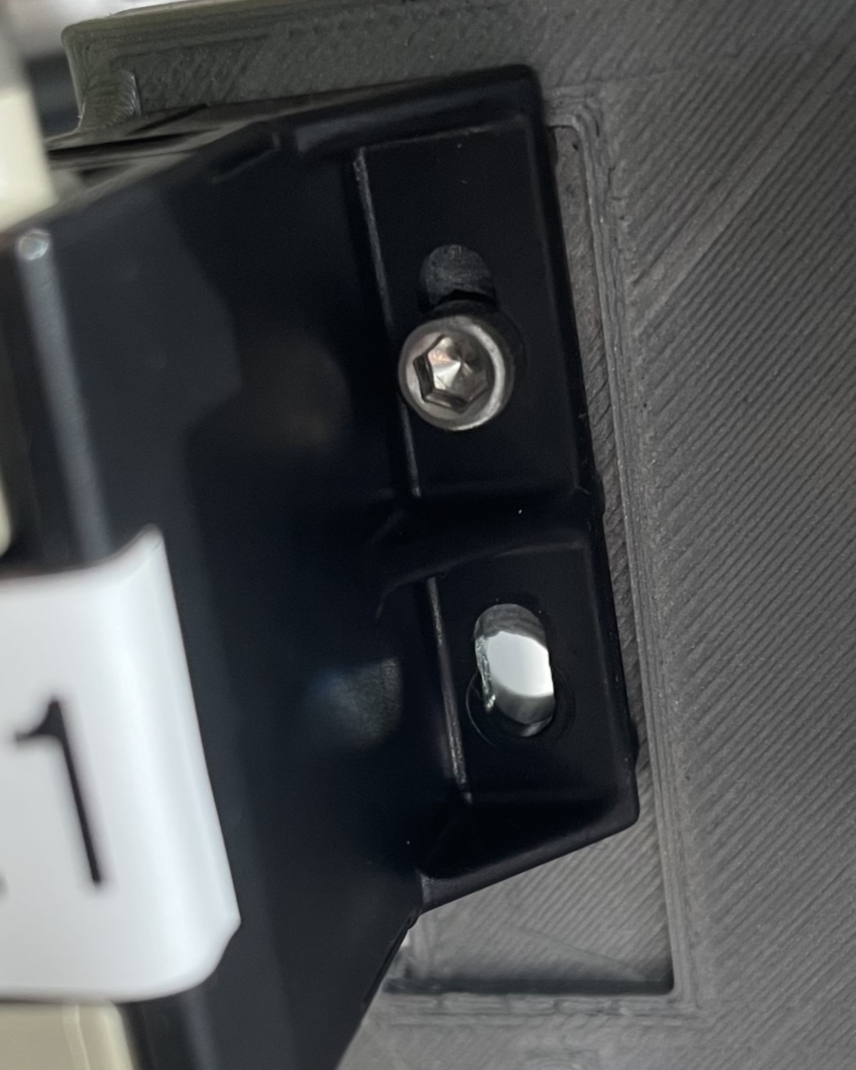
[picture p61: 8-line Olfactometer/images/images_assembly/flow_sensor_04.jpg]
    
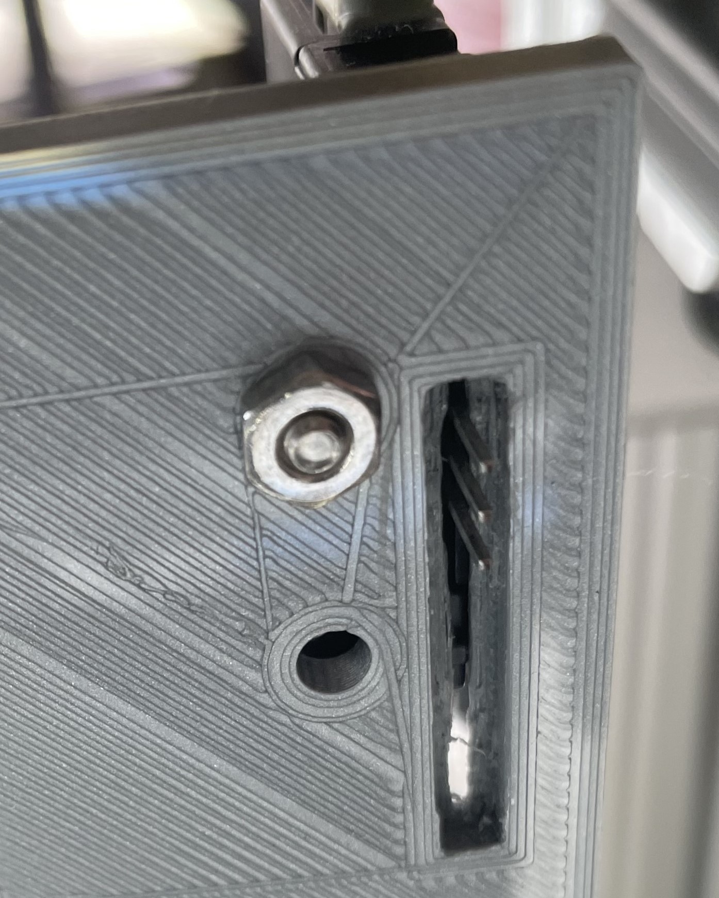
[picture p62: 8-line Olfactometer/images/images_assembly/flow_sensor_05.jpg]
    
</p>

- Loosen the (x2) 4-40 screws through the main manifold/main manifold cover, and pull the flow sensor down until it is disconnected


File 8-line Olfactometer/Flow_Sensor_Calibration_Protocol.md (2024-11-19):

# Flow Sensor Calibration

To ensure accurate flow readings, each flow sensor should be individually calibrated before use.  

The calibration table for each flow sensor csv file contains **flow rates** (in SCCM) and the corresponding **flow sensor value** (as an integer from 0-1023).  

*<p align="center">*Example calibration table:*</p>*
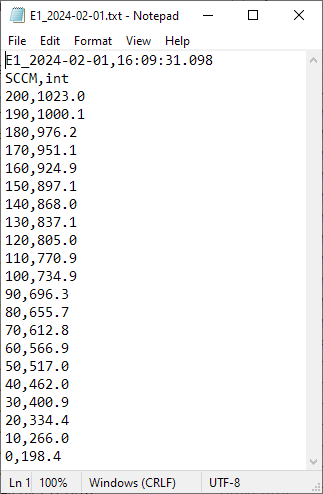
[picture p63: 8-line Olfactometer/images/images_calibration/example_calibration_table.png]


<br>

## Hardware setup

***Note**:* With the current system, the most efficient way to calibrate new flow sensors is prior to installation onto the main manifold. Calibrating while sensors are installed on the manifold can be more time consuming (due to pressure changes when changing setpoints), so use your own discretion on which method to use (depending on how many flow sensors need to be calibrated.)  

<br>

### Setup options:

### **A. On Manifold** (Flow sensor still installed on olfactometer manifold)  
&nbsp;&nbsp;&nbsp;&nbsp;***Recommended when calibrating 1-2 flow sensors***  
&nbsp;&nbsp;&nbsp;&nbsp;Example use: Recalibrating/checking calibration of currently installed flow sensors  
<br>
The hardware setup must be modified to ensure the entirety of the Alicat MFC output passes through the flow sensor being calibrated.  

<br>
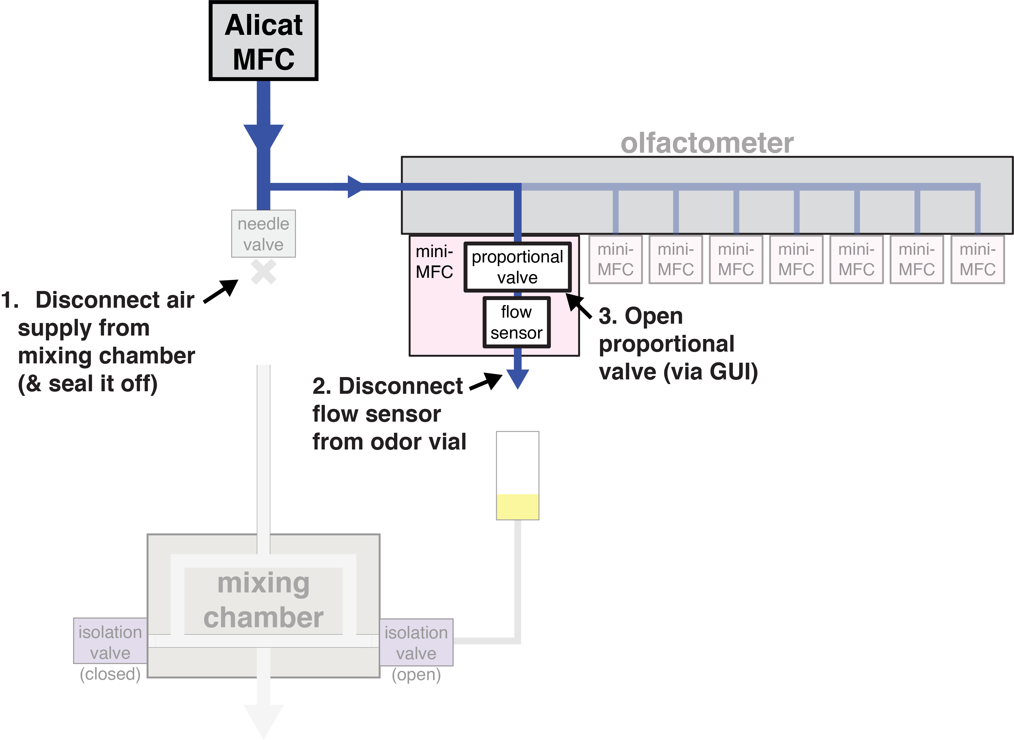
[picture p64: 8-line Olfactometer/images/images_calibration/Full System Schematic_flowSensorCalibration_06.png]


1. Disconnect the tubing that connects the Alicat MFC to the mixing chamber, and plug the open fitting. (This ensures that all air from the Alicat MFC passes through the olfactometer manifold.)

2. Disconnect the flow sensor from the odor vial. This allows the air to pass freely through the flow sensor, without anything blocking the output. (Easiest way to do this is to twist the needle, disconnecting it from the luer fitting on the flow sensor tubing.)

3. Fully open the proportional valve via the olfactometer GUI. (This, once again, ensures that all air will pass through the flow sensor.)
	- Open the "Vial Details" popup window for the line to be calibrated.
	- Select "Enable Manual Options".
	- In the "Manual Controls" box, enter "255" next to the "Set prop valve" button.
	- Click "Set prop valve".

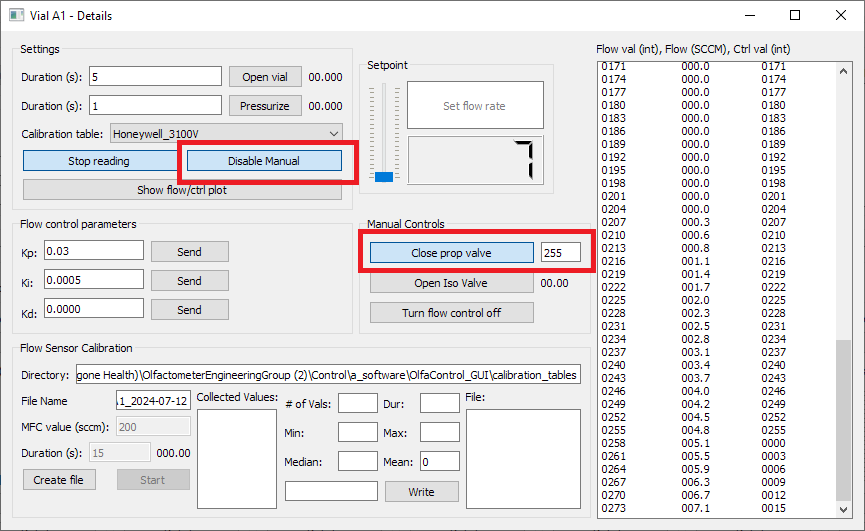
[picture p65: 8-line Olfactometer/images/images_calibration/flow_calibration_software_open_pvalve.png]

<br>

### **B. Off Manifold**  
&nbsp;&nbsp;&nbsp;&nbsp;***Recommended when calibrating 4+ flow sensors***  
&nbsp;&nbsp;&nbsp;&nbsp;Example use: New sensors that have not been installed yet

1. Connect the MFC input to an air supply.  
2. Connect the MFC output directly to the flow sensor input. (Flow sensor works well with 1/8" ID flexible tubing, which can be slid over 1/8" OD Teflon tubing to make a sufficiently airtight seal for this application).  
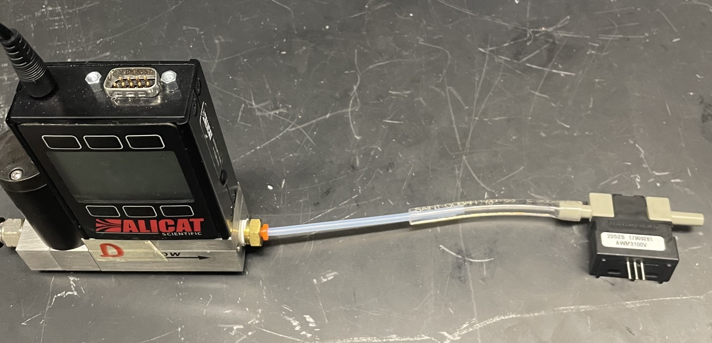
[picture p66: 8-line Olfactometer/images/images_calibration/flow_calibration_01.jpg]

<br>

3. Connect the flow sensor to the Olfactometer PCB (either directly, or using jumper wires, whichever is more convenient).  
<p align="center">
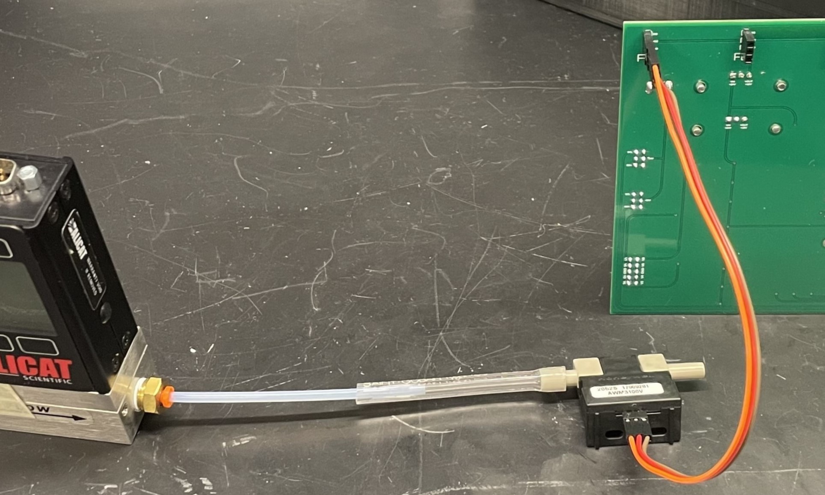
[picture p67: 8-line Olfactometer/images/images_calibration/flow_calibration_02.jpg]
    
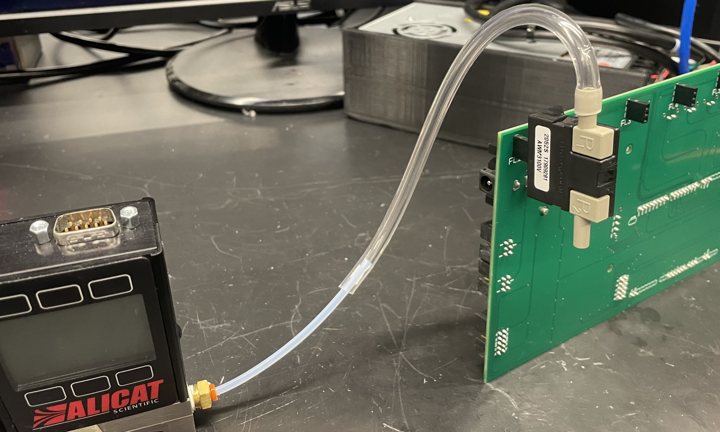
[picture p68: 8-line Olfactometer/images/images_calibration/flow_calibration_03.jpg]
    
</p>

4. Connect the Olfactometer PCB to the computer and 24V power supply as usual.  
<br>

## Software

### Create File

1. Open the Olfactometer GUI and connect to the device.  
2. Open the Vial Details box for the selected flow sensor.  
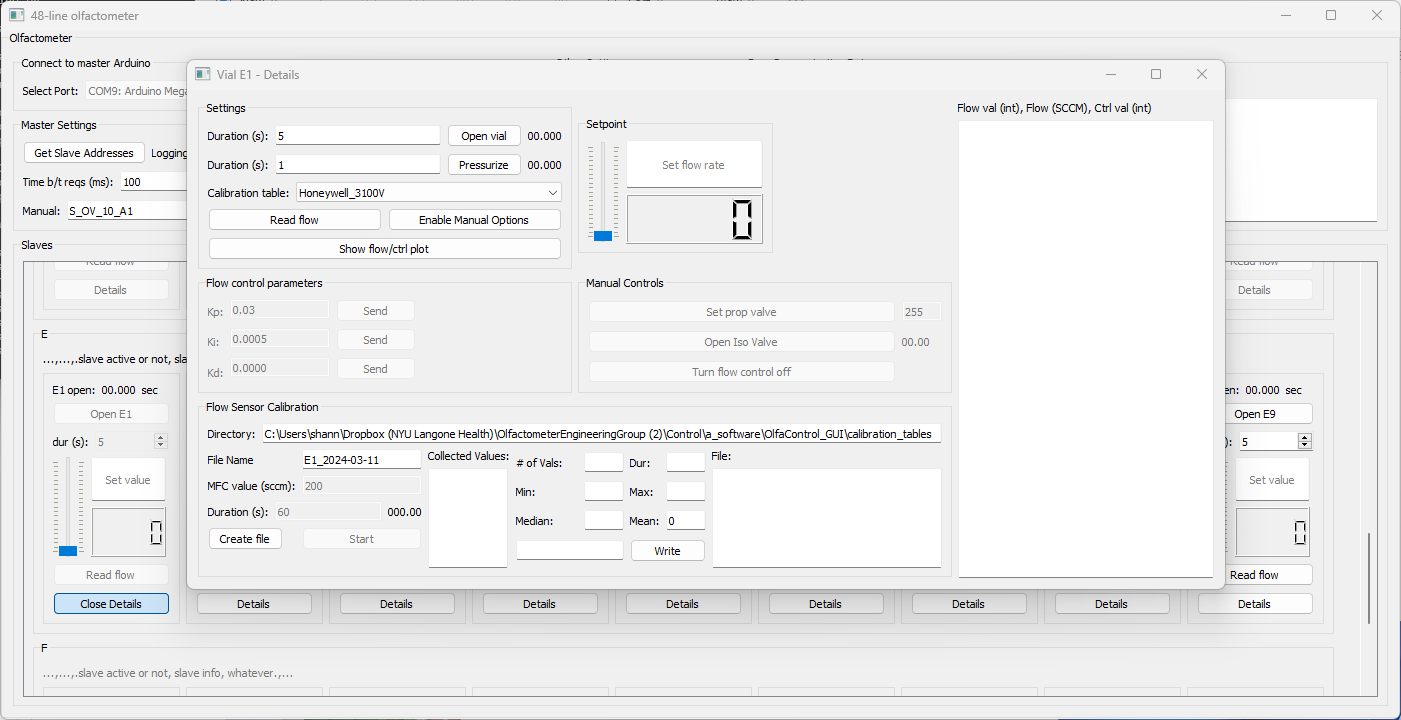
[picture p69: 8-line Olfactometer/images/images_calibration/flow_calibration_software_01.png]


3. Confirm/edit the calibration table directory and enter the desired file name.  
4. Click "Create File". (This will create the file and set the flow sensor to "debug" mode, if it is not already.)  


<br>

## Calibrate

***Note:** Calibration tables **must** be in descending order, so it is recommended to start calibrating at the maximum capacity and work down from there. Otherwise, the table will need to be sorted manually after completing the calibration.*  

1. Physically set the Alicat MFC to the first desired calibration value. (Ideally, the maximum capacity of the flow sensor: 200 sccm.) Enter that same value into the "MFC value (sccm)" box.  
&nbsp;&nbsp;&nbsp;**Note:** If calibrating with setup *A: On Manifold*, the Alicat MFC may not be able to reach 200 sccm (due to high impedance within the olfactometer manifold). If this is the case, start calibration at the highest flow rate the Alicat MFC is able to maintain in this setup (at least 120 sccm is ideal).    

2. Enter the desired duration of the calibration. (15 seconds is typically sufficient for off-manifold calibration, 30 seconds may be necessary for on-manifold calibration.)  



3. Click "Start".  

4. Once calibration at this flow rate is complete, stats about the flow sensor data collected during that period will populate the fields in the center of the groupbox. By default, the values to write to the calibration files will display in the bottom-right box (*flow rate* [SCCM], *mean value* [integer]).  
&nbsp;&nbsp;&nbsp;**Note:** Don't worry about the SCCM flow rate displayed in the "Setpoint" box - this is based on whatever calibration table is currently selected, and is likely inaccurate.  



5. **Check if the calibration was successful** by looking at the range of values collected from the flow sensor during the calibration. If the range exceeds 4, repeated trials are recommended.  

&nbsp;&nbsp;&nbsp;&nbsp;&nbsp;&nbsp;&nbsp;&nbsp;&nbsp;&nbsp;&nbsp;&nbsp;&nbsp;&nbsp;**Note:** Typically, at a single flow value, I run two 15-second calibrations and save the mean of the second one. If the means of the two calibrations differ by more than **1.0 on manifold** or more than **0.5 off manifold**, I recommend running additional 15-second calibrations until consecutive calibrations have similar values.  (For setup *A: On Manifold*, when the Alicat MFC value is changed, the pressure within the system can take 1-2 minutes to stabilize, which affects the flow sensor readout. This setup typically requires many more consecutive trials until the system has reached stability.)  

<br>

6. If the calibration was successful, click the "Write" button to write this pair to the calibration file. If necessary, you can also manually enter the values to write to the file. (Values already written to the file will be displayed in the far right box.)  

7. **Repeat for as many values as desired.** (I typically do 10sccm increments, to save time. For more sensitive experiments, 2-5 increments may be more helpful.)

<br>

## Once complete:

1. Click "End & Save File"
2. Go to the calibration table directory, and change the file extension from .csv to .txt. (Ignore any warnings about the file becoming unusable.)
3. Update the olfa_config file (using any text editor) to include the name of the new calibration table.

*<p align="center">*Example olfa_config file:*</p>*


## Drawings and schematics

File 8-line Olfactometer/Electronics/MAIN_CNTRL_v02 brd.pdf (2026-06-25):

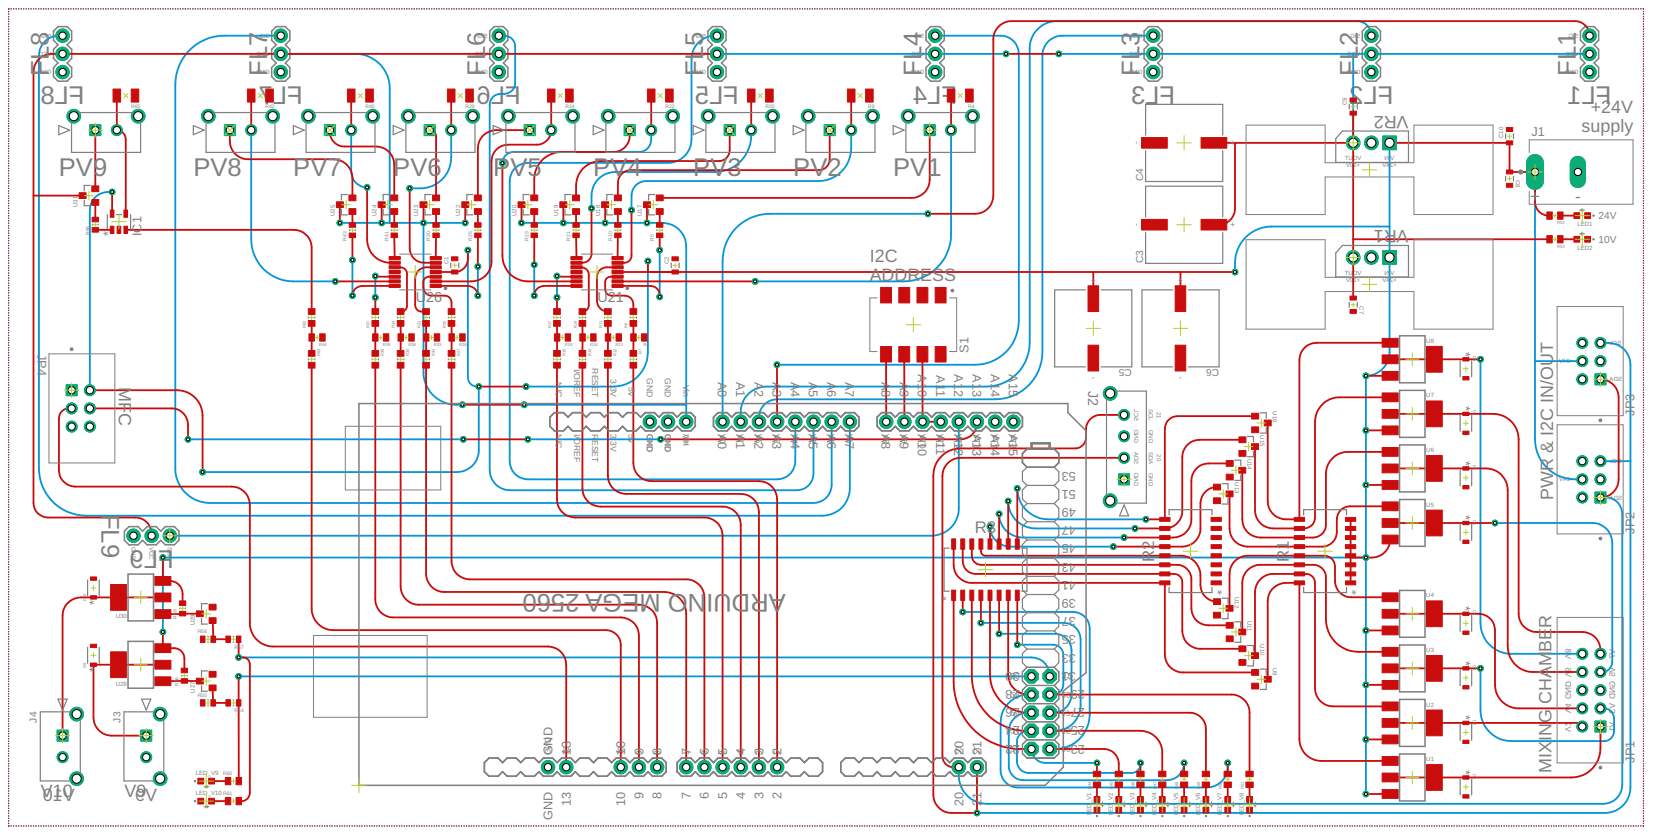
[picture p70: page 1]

8LF 7LF 6LF 5LF 4LF 3LF 2LF 1LF 9LF GND GND SCL SDA V42+ ADS L CS TUOV NI V V4 V1V2 V8 V6V5 V7 V3 V42+ ADS L CS 01V 9V GNDGND V01+ V42+ TUOV NI V V01+ V42+ 198765432020212224262830 31 A0A1A2A3A4A5A6A7A8A9A10 A11 A12 A13 A14 A15 GND GND Vin GND23252729 13 GI S CCV DNG GI S CCV DNG GI S CCV DNG GI S CCV DNG GI S CCV DNG GI S CCV DNG GI S CCV DNG GI S CCV DNG +24V supply PWR & I2C IN/OUT 24V 10V V10 V9 MFC MIXING CHAMBER I2CADDRESS 21 20 GND GND SCL SDA 19876543201320212242628203 133353739314345474941535 A0A1A2A3A4A5A6A7A8A9A10 A11 A12 A13 A14 A15 RESET 3.3V 5VGND GND Vin GND 0652 AGE M ONI UDRA I/OREF N/C 92725232 98765432102021 GND A0A1A2A3A4A5A6A7A8A9 A10 A11 A12 A13 A14 A15 RESET 3.3V5V GND GNDVin I/OREF N/C 13 * * * -+ -+ -+ -+ * * * * * * * * + - * * SIGVCC GND * R1 R10 R11 R12 R13 R14 R15 R16 R17 R18 R19 R2 R20 R21 R22 R23 R3 R4 R5 R6 R7 R8 R9 U1 U10 U11 U12 U13 U14 U15 U16 U17 U18 U19 U2 U20 U3 U4 U5 U6 U7 U8 U9 U21 PV4 PV3 PV2 S1 JP1 LED_V1 R44 LED_V2 R45 R46 LED_V3 R47 LED_V4 LED_V5 R48 LED_V6 R49 R50 LED_V7 R51 LED_V8 C1 C9 C8 C10 R52 LED1 R53 LED2 C3 C4 5 C 6 C D1 D2 D3 D4 D5 D6 D7 D8 J2 J1 R54 R55 U2U28 R756 D9 R57 R58 U2U30 R959 D10 FL1 FL2 FL3 FL4 FL5 FL6 FL7 FL8 U22 R24 U26 R25 R26 R27 R28 U23 R29 R30 R31 R32 R33 R34 R35 R36 R37 R38 R39 U24 R41 U25 R42 R43 C2 PV8 PV7 PV6 PV5 R40 FL9 LED_V9 R60 LED_V10 R61 1 RV C7 2 RV R62 R63 R64 U31 R65 R66 PV9 JP3 JP2 J3J4 IC1 JP4 PV1

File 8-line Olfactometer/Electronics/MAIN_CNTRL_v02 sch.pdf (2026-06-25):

A

A

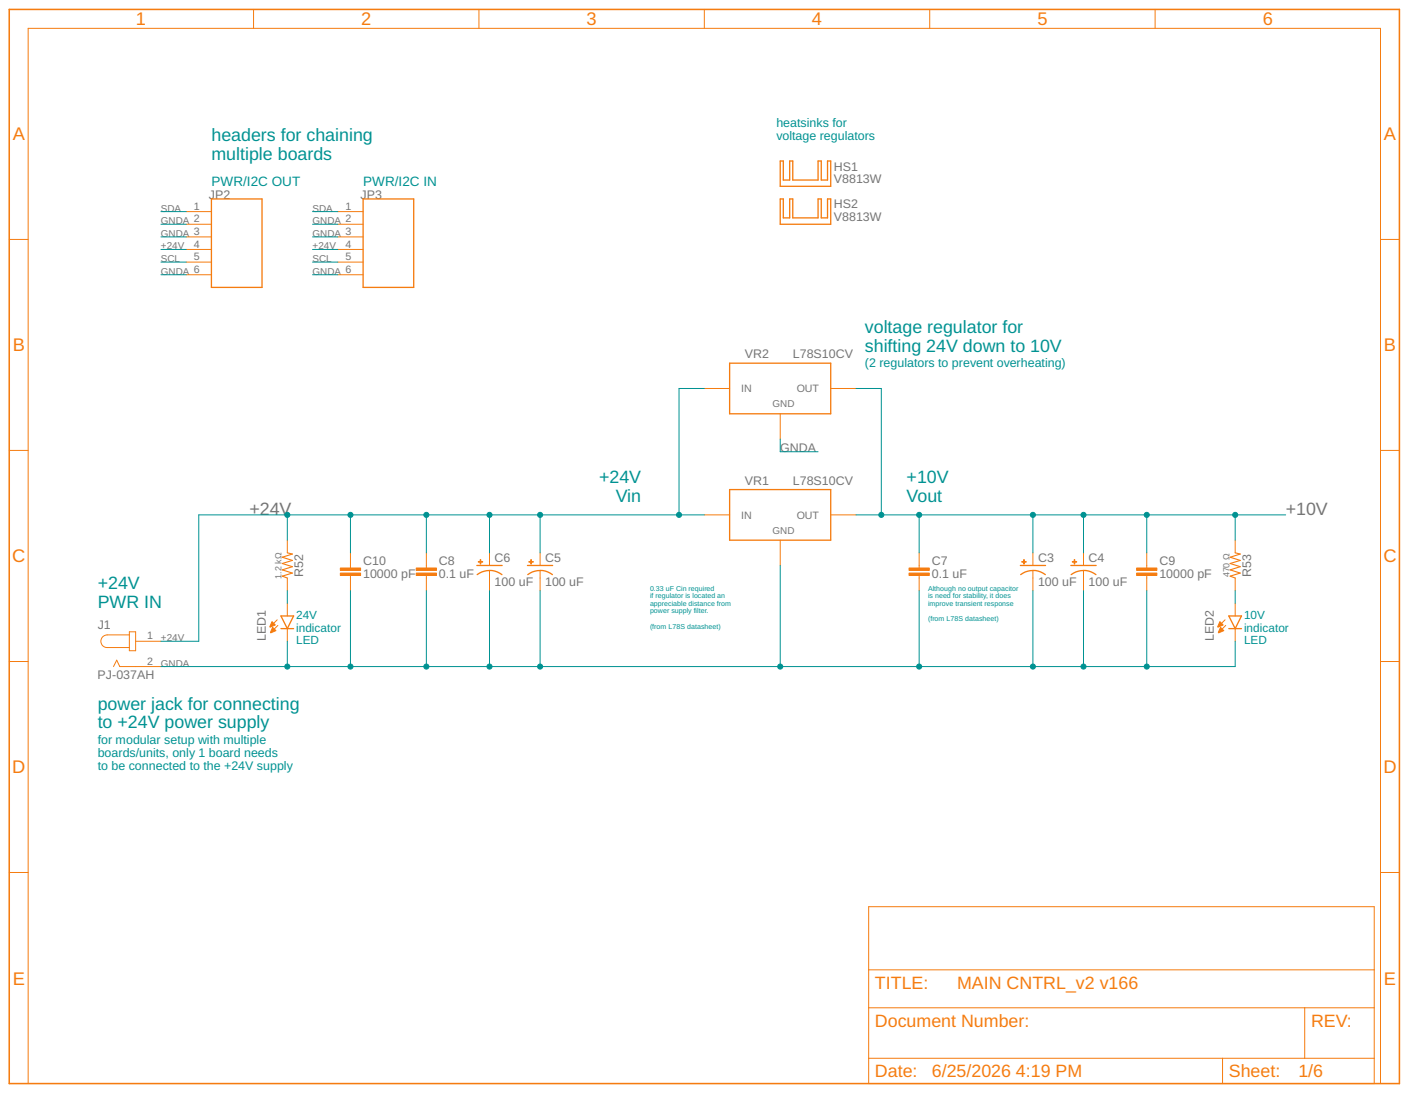
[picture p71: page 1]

heatsinks for voltage regulators

voltage regulator for
shifting 24V down to 10V
(2 regulators to prevent overheating)

0.33 uF Cin required
if regulator is located an
appreciable distance from
power supply filter. (from L78S datasheet)

Although no output capacitor
is need for stability, it does
improve transient response
(from L78S datasheet)

power jack for connecting
to +24V power supply
for modular setup with multiple
boards/units, only 1 board needs
to be connected to the +24V supply

Document Number: | REV:

Date: 6/25/2026 4:19 PM | Sheet: 1/6

1-1825059-7 GNDA 9 9 8 8 7 7 6 6 5 5 4 4 3 3 2 2 A5A4A3A2A1A0VIN GND 20(SDA) 20 21(SCL) 21 A11 A10 A9A8A6A7 232527 2928262422 A12 A13 A14 A15 3130 10 10 13 13 S1 87 12 65 34 J2 1234 FL1123 FL2123 FL3123 FL4123 FL5123 FL6123 FL7123 FL8123 N$A0 N$A0 N$A1 N$A1 N$A3 N$A3 N$A5 N$A5 N$A6 N$A6 N$A7 N$A7 N$A10 N$A8 N$A9 GNDA GNDA GNDA GNDA GNDA GNDA GNDA GNDA GNDA GNDA GNDA P7P8P6P5P4P3P2P1 SDA +10V +10V +10V +10V +10V +10V +10V +10V +10V V1V2V3V4V5V6V7V8 SCL N$A2 N$A2 N$A12 V9V10 N$A4 N$A4 P9 N$A13 MFC_AIN ARDUINO MEGA 2560 sig vcc gnd sig vcc gnd sig vcc gnd sig vcc gnd sig vcc gnd sig vcc gnd sig vcc gnd sig vcc gnd ABCDE ABCDE 1 2 3 4 5 6 6/25/2026 4:19 PM 2/6 MAIN CNTRL_v2 v166 Date: Sheet: REV: TITLE: Document Number: I2CADDRESS SELECT SLAVE MEGA. USE 0.1" (2.54 MM) MALE HEADERS FROM PCB TO FEMALE HEADERS ON MEGA BOARD HEADER FOR MASTER I2C PINS PLEASE NOTE THAT ALL SLAVE I2C PULLUP RESISTORS SHOULD BE REMOVED BEFORE INTERCONNECTION WITH OTHER BOARDS AND MASTER HEADER PINS FOR FLOW SENSORS TO PROPORTIONAL VALVE CIRCUITRY TO ISOLATION VALVE CIRCUITRY ADDITIONAL FLOW SENSOR ADDITIONAL +24V ISOLATION VALVES ADDITIONAL PROPORTIONAL VALVE MFC Analog Input (receive from MFC) PWM output to MFC (send to MFC)

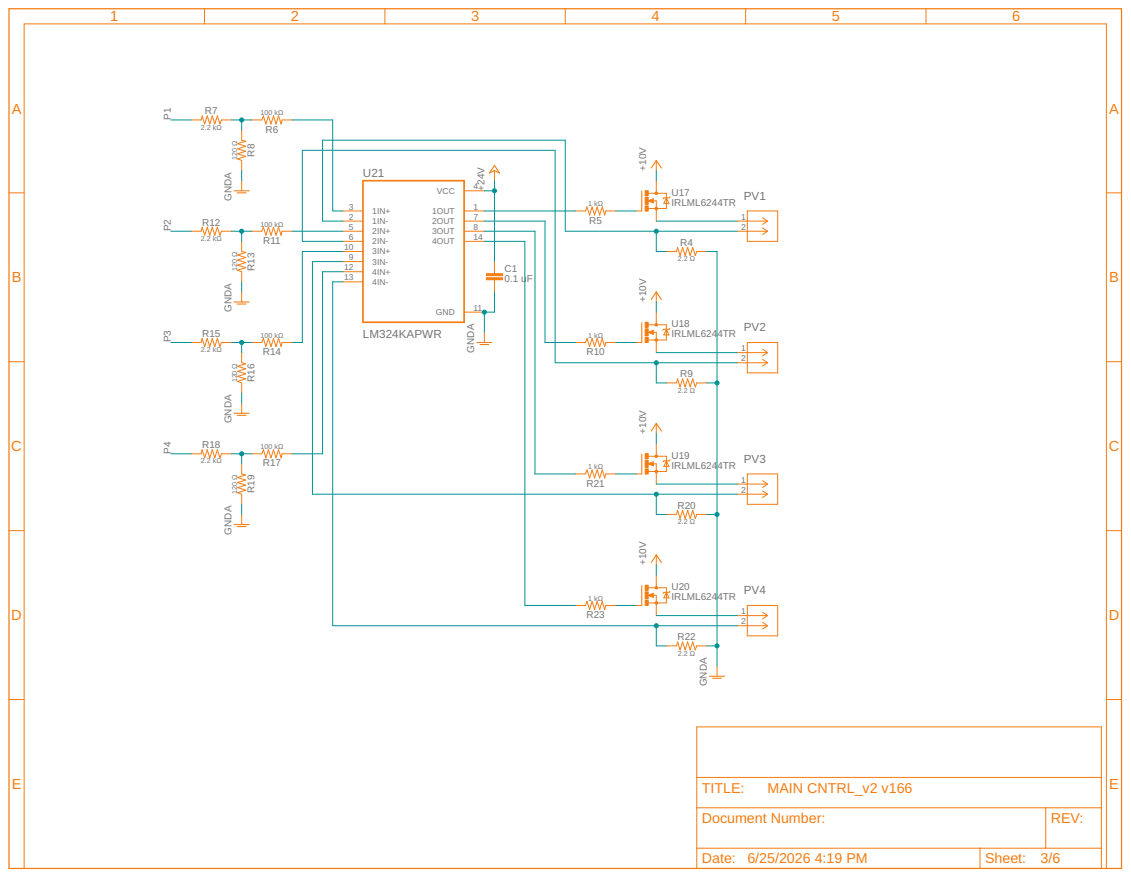
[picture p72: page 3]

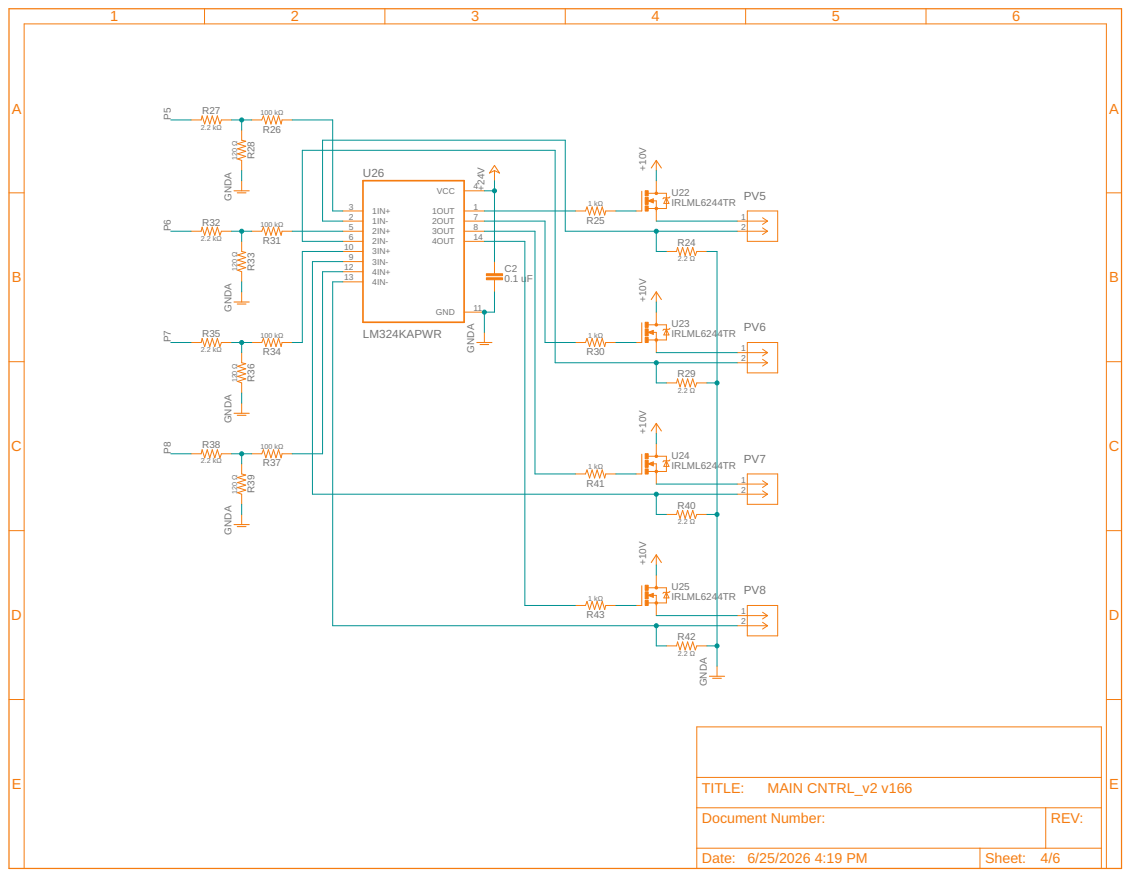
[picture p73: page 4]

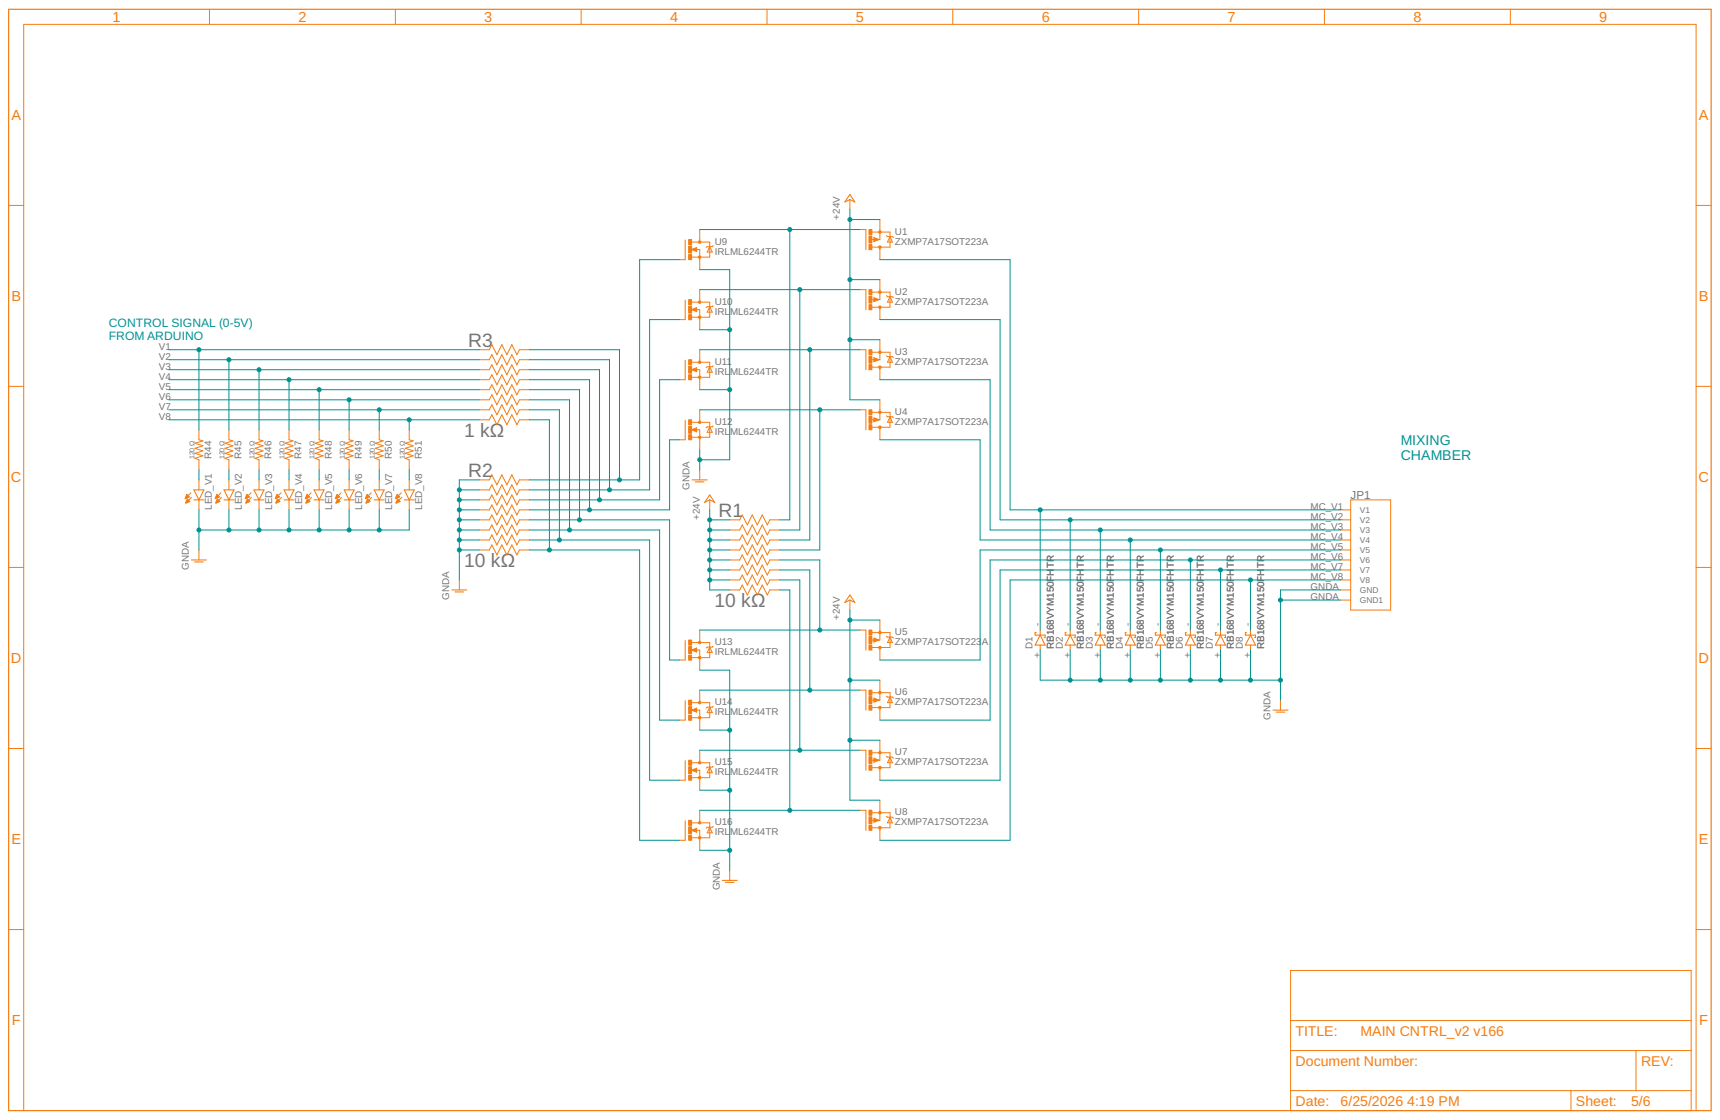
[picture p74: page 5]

CONTROL SIGNAL (0-5V) FROM ARDUINO

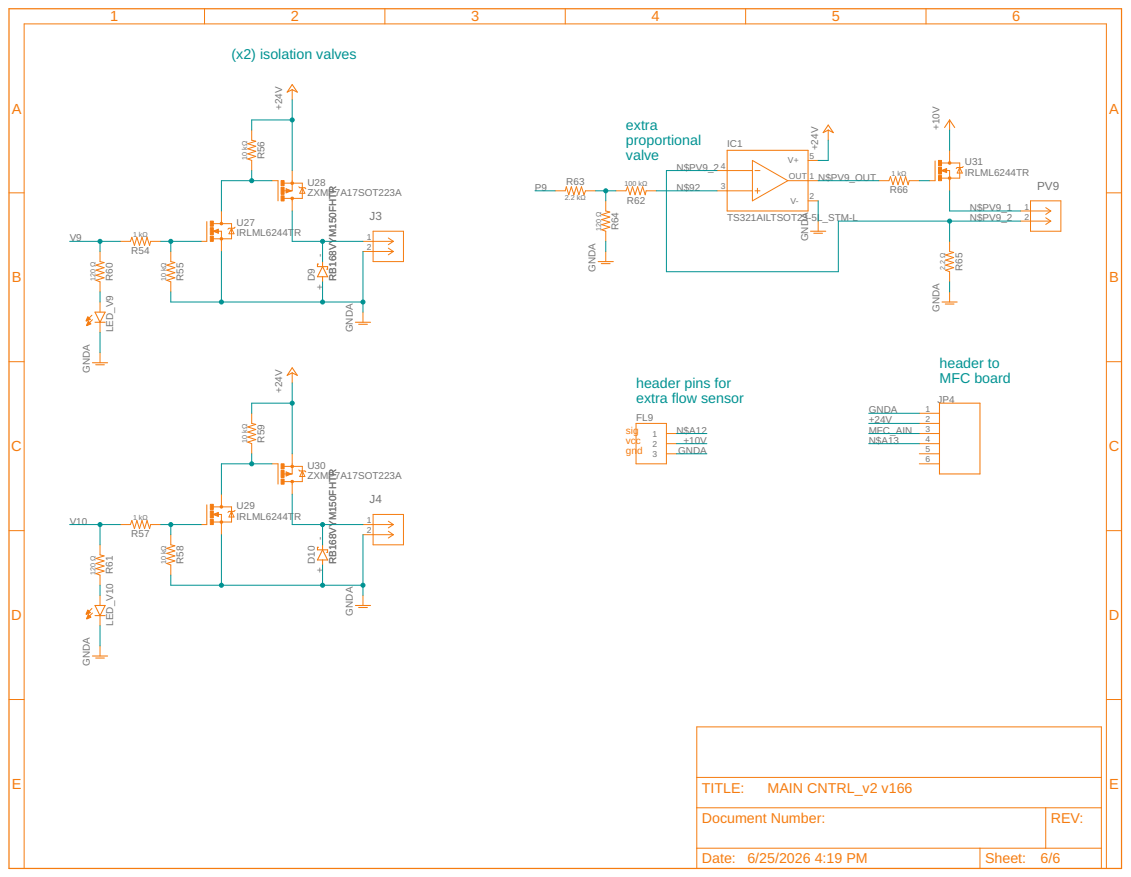
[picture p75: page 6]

+ - + - OUT 1 kΩ 10 kΩ IRLML6244TR ZXMP7A17SOT223A 10 kΩ RB168VYM150FHTR RB168VYM150FHTR +24V 1 kΩ 10 kΩ IRLML6244TR ZXMP7A17SOT223A 10 kΩ RB168VYM150FHTR RB168VYM150FHTR +24V GNDA GNDA 120 Ω 120 Ω GNDA GNDA 100 kΩ 2.2 kΩ 120 Ω GNDA IRLML6244TR 2.2 Ω GNDA 1 kΩ +10V +24V GNDTS321AILTSOT23A-5L_STM-L R54 R55 U27 U28 R56 D9 R57 R58 U29 U30 R59 D10 FL9123 LED_V9 R60 LED_V10 R61 R62 R63 R64 U31 R65 R66 PV9 1 J3 2 12J4 12 IC1 43 1 V+ 5 V- 2 JP4 123456 GNDA GNDA +24V +10V N$A12 V9V10 P9 N$PV9_OUT N$PV9_1 N$PV9_2 N$PV9_2 N$92 N$A13 MFC_AIN ABCDE ABCDE 1 2 3 4 5 6 6/25/2026 4:19 PM 6/6 MAIN CNTRL_v2 v166 Date: Sheet: REV: TITLE: Document Number: sig vcc gndheader pins for extra flow sensor (x2) isolation valves extra proportional valve header to MFC board

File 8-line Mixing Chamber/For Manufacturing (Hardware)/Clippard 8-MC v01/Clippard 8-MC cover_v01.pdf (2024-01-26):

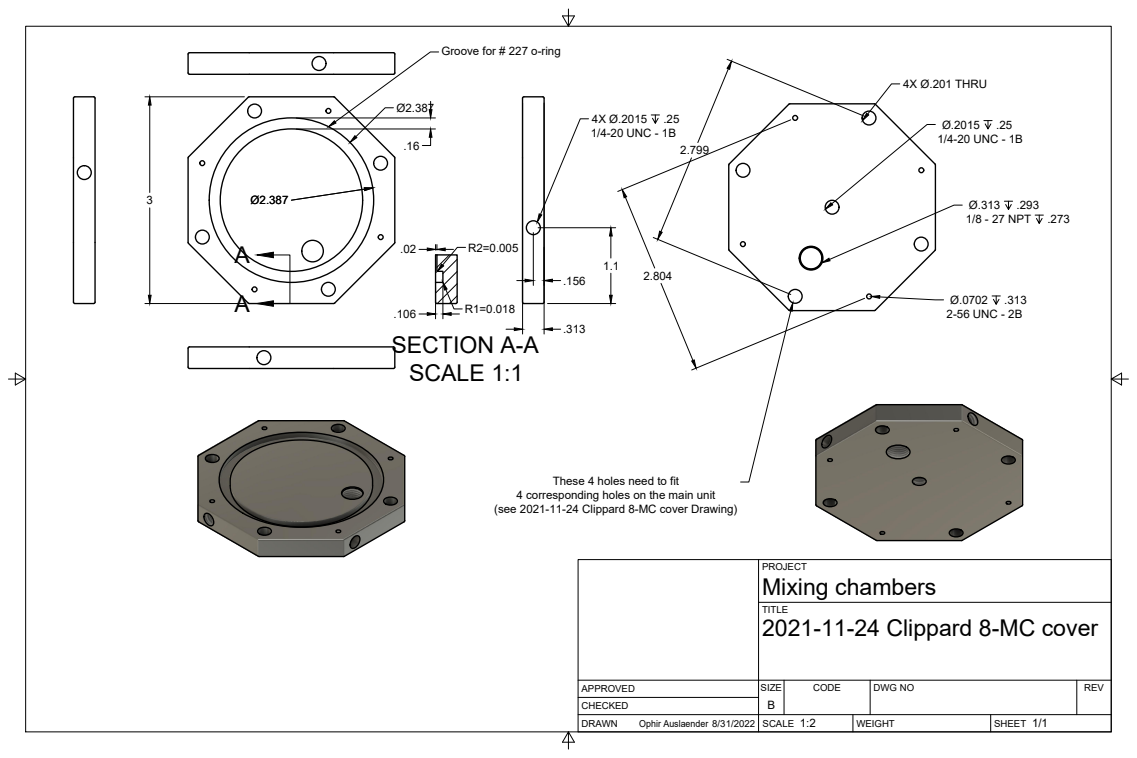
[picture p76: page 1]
TITLE; DRAWN; CHECKED; APPROVED; SCALE; WEIGHT; SHEET; SIZE; CODE; DWG NO; REV; Ophir Auslaender 8/31/2022; 1/4-20 UNC - 1B; 1/8 - 27 NPT; 4X Ø.201 THRU; 2-56 UNC - 2B; SECTION A-A SCALE 1:1

Groove for # 227 o-ring

These 4 holes need to fit

4 corresponding holes on the main unit
(see 2021-11-24 Clippard 8-MC cover Drawing)

PROJECT
Mixing chambers
2021-11-24 Clippard 8-MC cover

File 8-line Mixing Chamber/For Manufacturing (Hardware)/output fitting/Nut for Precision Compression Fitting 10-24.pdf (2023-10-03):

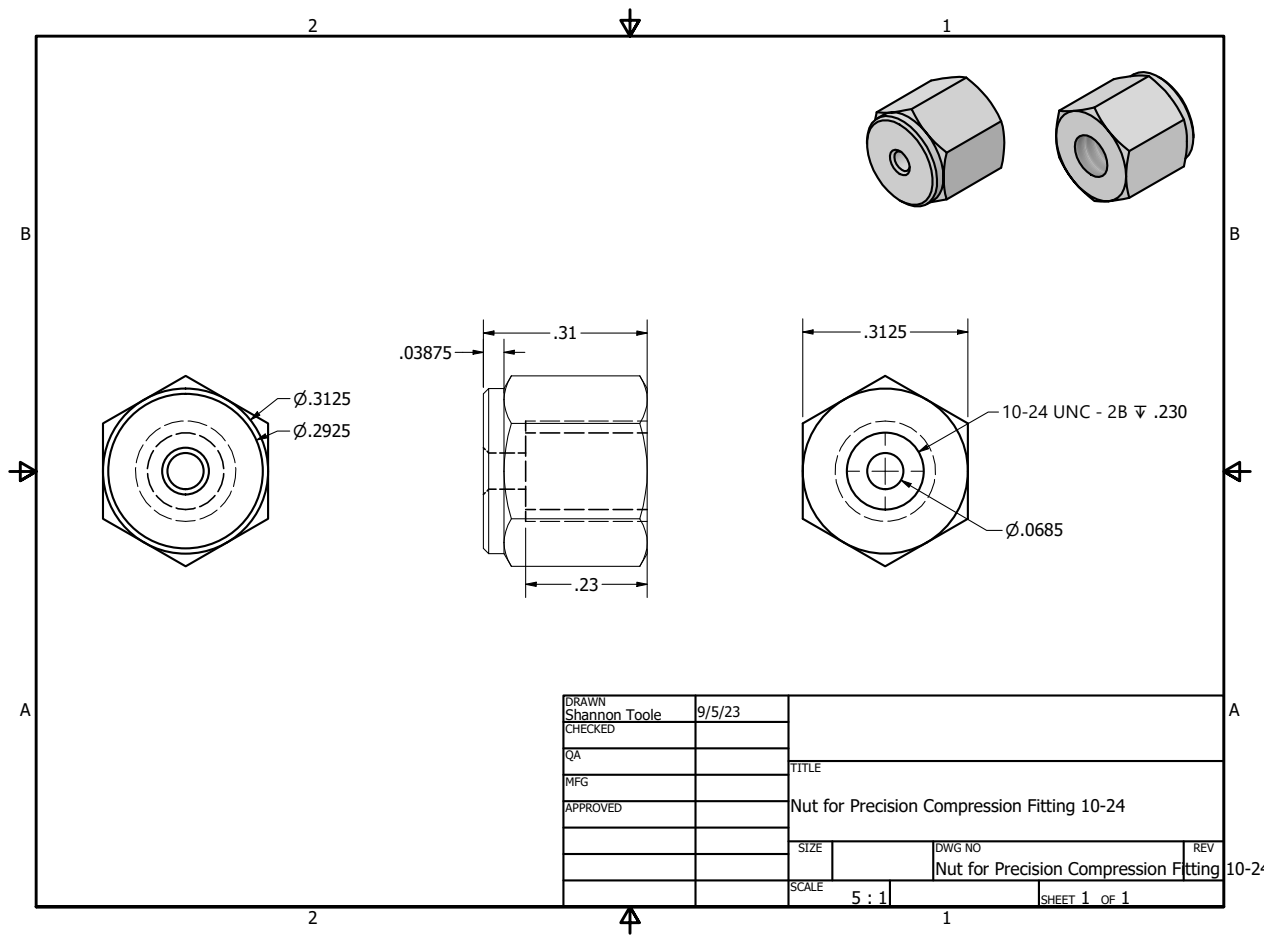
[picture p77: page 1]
Nut for Precision Compression Fitting; 10-24 UNC - 2B ↧ .230

DRAWN Shannon Toole | 9/5/23

CHECKED

MFG

Nut for Precision Compression Fitting 10-24

APPROVED

SIZE | DWG NO | REV

SCALE 5 : 1 | | SHEET 1 OF 1

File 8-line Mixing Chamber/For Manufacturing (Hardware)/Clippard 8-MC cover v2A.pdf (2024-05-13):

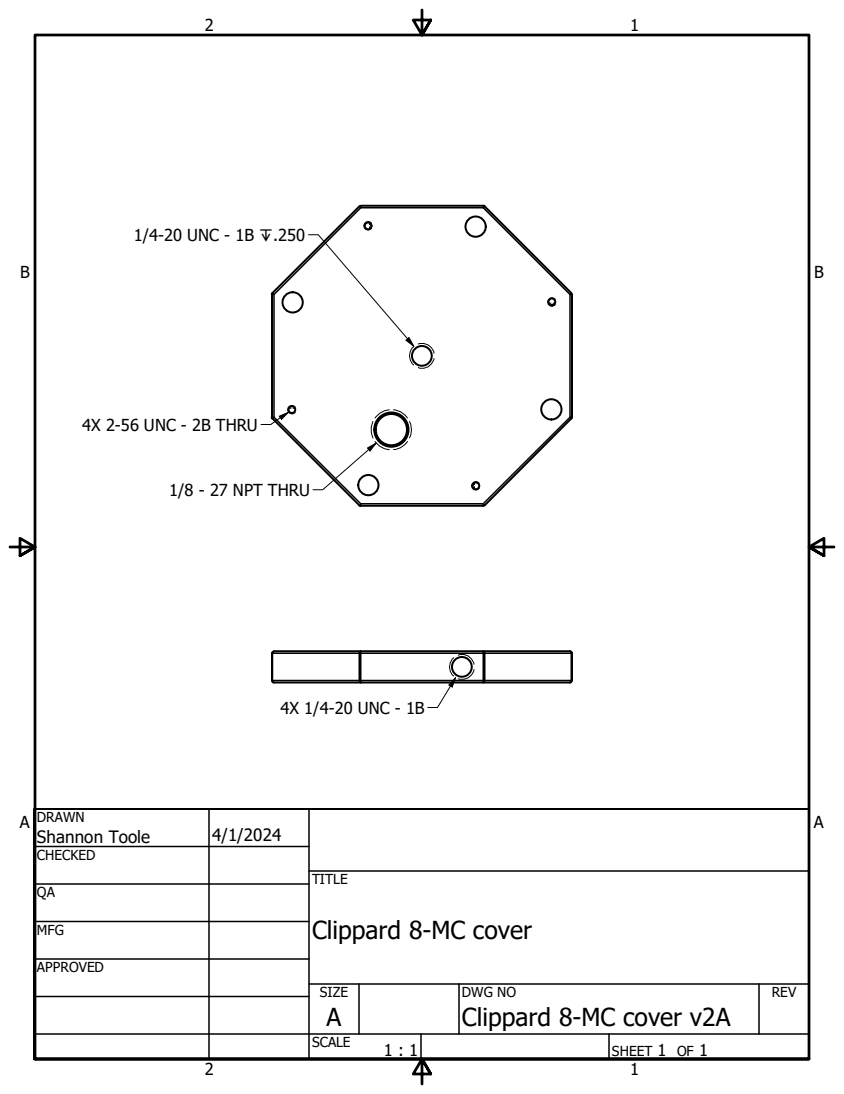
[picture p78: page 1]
1/8 - 27 NPT THRU; 4X 2-56 UNC - 2B THRU; 1/4-20 UNC - 1B ↧.250; 4X 1/4-20 UNC - 1B

DRAWN Shannon Toole | 4/1/2024

CHECKED

MFG

Clippard 8-MC cover

APPROVED

SIZE A | DWG NO Clippard 8-MC cover v2A | REV

SCALE 1 : 1 | | SHEET 1 OF 1

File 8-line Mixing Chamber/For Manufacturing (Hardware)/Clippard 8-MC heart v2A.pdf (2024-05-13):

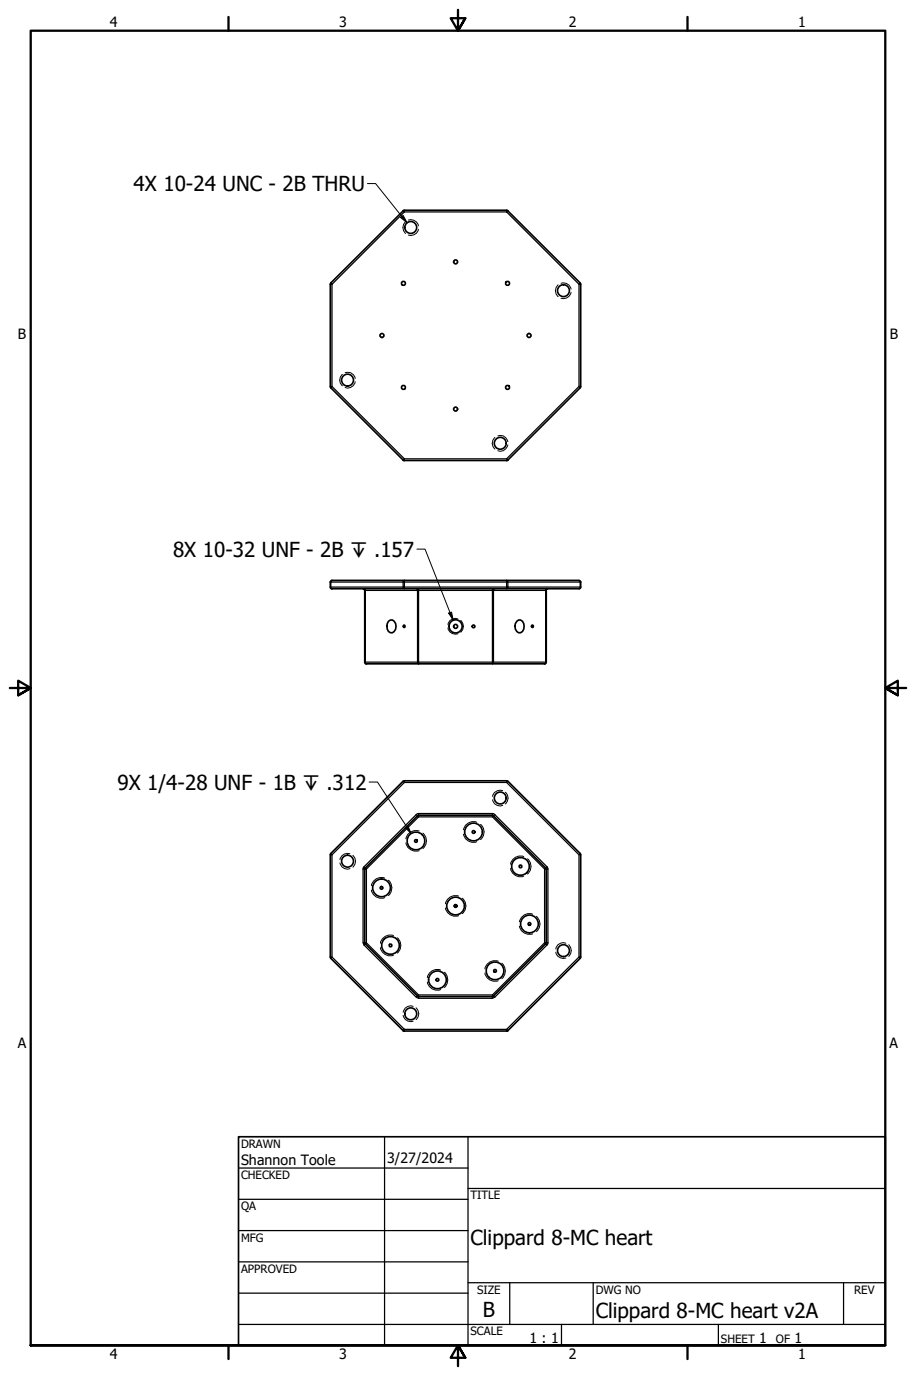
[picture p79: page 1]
9X 1/4-28 UNF - 1B ↧ .312; 4X 10-24 UNC - 2B THRU; 8X 10-32 UNF - 2B ↧ .157

DRAWN Shannon Toole | 3/27/2024

CHECKED

MFG

Clippard 8-MC heart

APPROVED

SIZE B | DWG NO Clippard 8-MC heart v2A | REV

SCALE 1 : 1 | | SHEET 1 OF 1

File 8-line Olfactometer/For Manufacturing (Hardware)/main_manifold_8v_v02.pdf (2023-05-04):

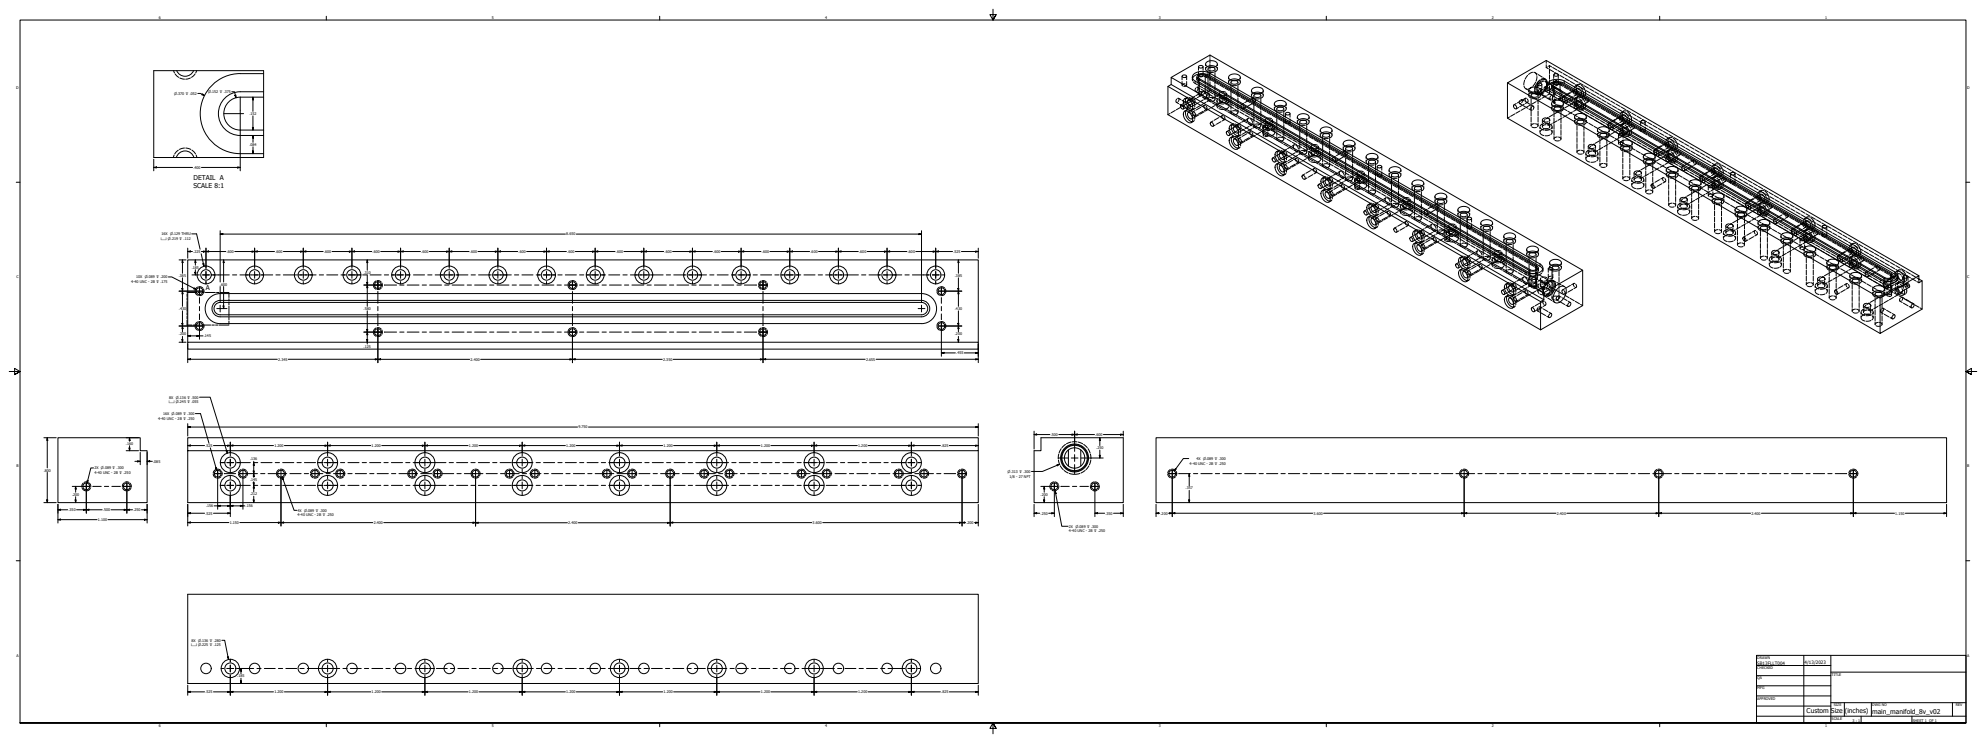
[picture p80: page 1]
DETAIL A SCALE 8:1; 16X ⌀.089 ↧ .300 4-40 UNC - 2B ↧ .250; 4X ⌀.089 ↧ .300 4-40 UNC - 2B ↧ .250; 16X ⌀.129 THRU ⌴ ⌀.219 ↧ .112; 10X ⌀.089 ↧ .200 4-40 UNC - 2B ↧ .175; 1/8 - 27 NPT; 2X ⌀.089 ↧ .300 4-40 UNC - 2B ↧ .250

DRAWN SB13FLLT004 | 4/13/2023

CHECKED

MFG

APPROVED

SIZE Size | (inches) | DWG NO main_manifold_8v_v02 | REV
Custom

SCALE 3 : 1 | SHEET 1 OF 1

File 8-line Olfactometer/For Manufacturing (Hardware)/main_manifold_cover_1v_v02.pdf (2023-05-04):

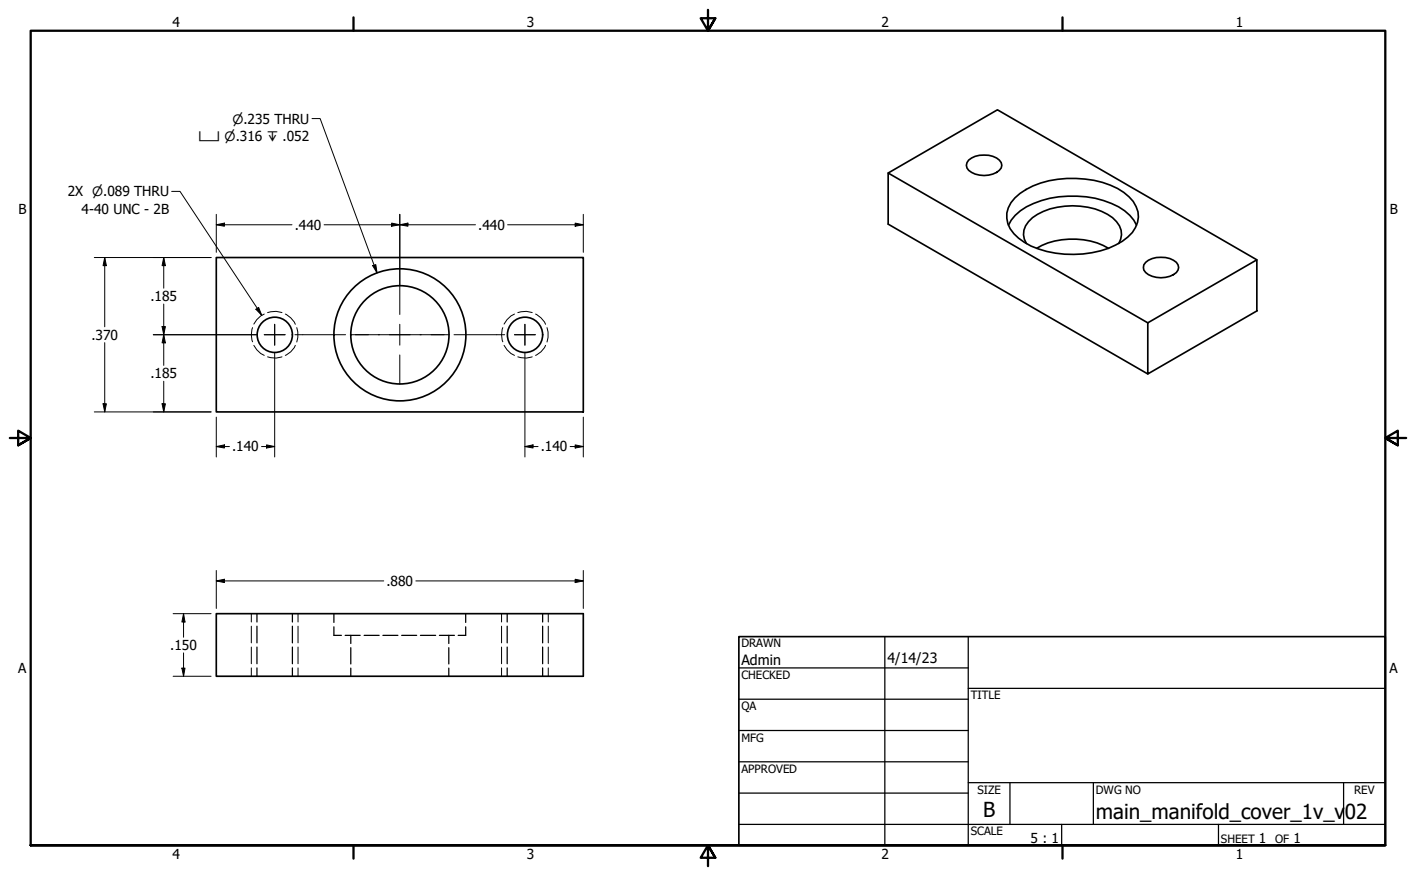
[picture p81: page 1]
2X ⌀.089 THRU; 4-40 UNC - 2B; ⌀.235 THRU ⌴ ⌀.316 ↧ .052

DRAWN Admin | 4/14/23

CHECKED

MFG

APPROVED

SIZE B | DWG NO main_manifold_cover_1v_v02 | REV

SCALE 5 : 1 | | SHEET 1 OF 1

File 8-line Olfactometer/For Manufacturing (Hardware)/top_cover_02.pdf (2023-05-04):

16X ⌀.219 THRU; 10X ⌀.129 THRU

DRAWN SB13FLLT004 | 4/18/2023

CHECKED

MFG

APPROVED

SIZE D | DWG NO top_cover_02 | REV

SCALE 3 : 1 | | SHEET 1 OF 1


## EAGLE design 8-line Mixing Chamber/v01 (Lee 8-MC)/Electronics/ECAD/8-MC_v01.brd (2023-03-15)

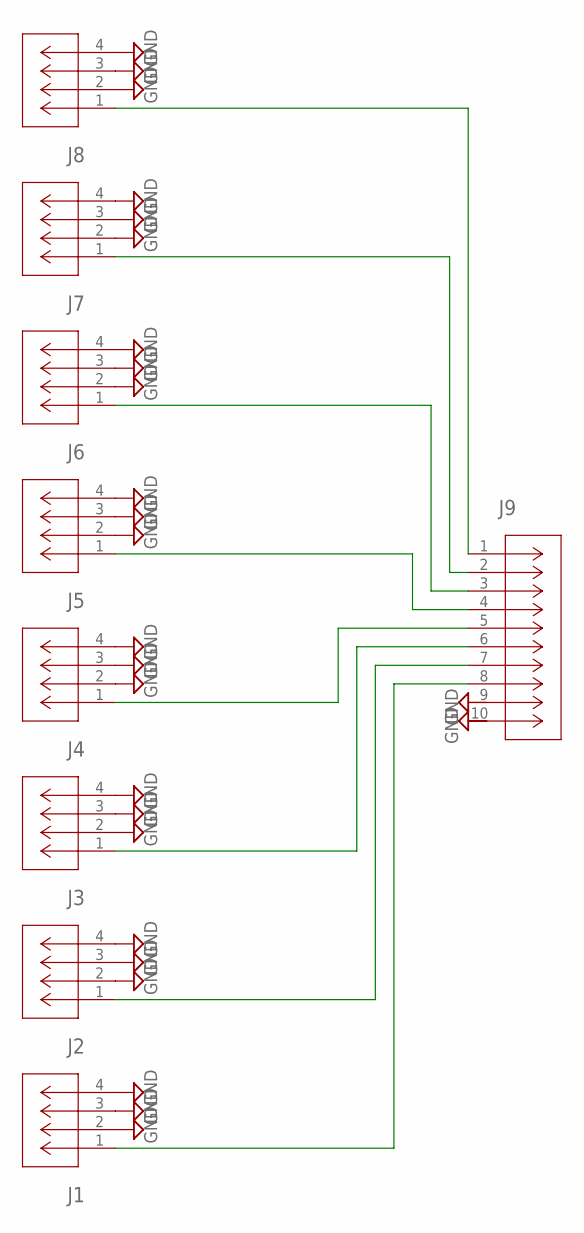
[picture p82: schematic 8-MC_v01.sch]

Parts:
J1, J2, J3, J4, J5, J6, J7, J8: 5055670281CON_5055670281; CON_5055670281
J9: FH52-10S-0.5SHCONN10_FH52-10S-0.5SH_HIR; CONN10_FH52-10S-0.5SH_HIR

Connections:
GND: J1.2, J1.3, J1.4, J2.2, J2.3, J2.4, J3.2, J3.3, J3.4, J4.2, J4.3, J4.4, J5.2, J5.3, J5.4, J6.2, J6.3, J6.4, J7.2, J7.3, J7.4, J8.2, J8.3, J8.4
unnamed: J8.1, J9.1
unnamed: J7.1, J9.2
unnamed: J6.1, J9.3
unnamed: J5.1, J9.4
unnamed: J1.1, J9.8
unnamed: J2.1, J9.7
unnamed: J3.1, J9.6
unnamed: J4.1, J9.5

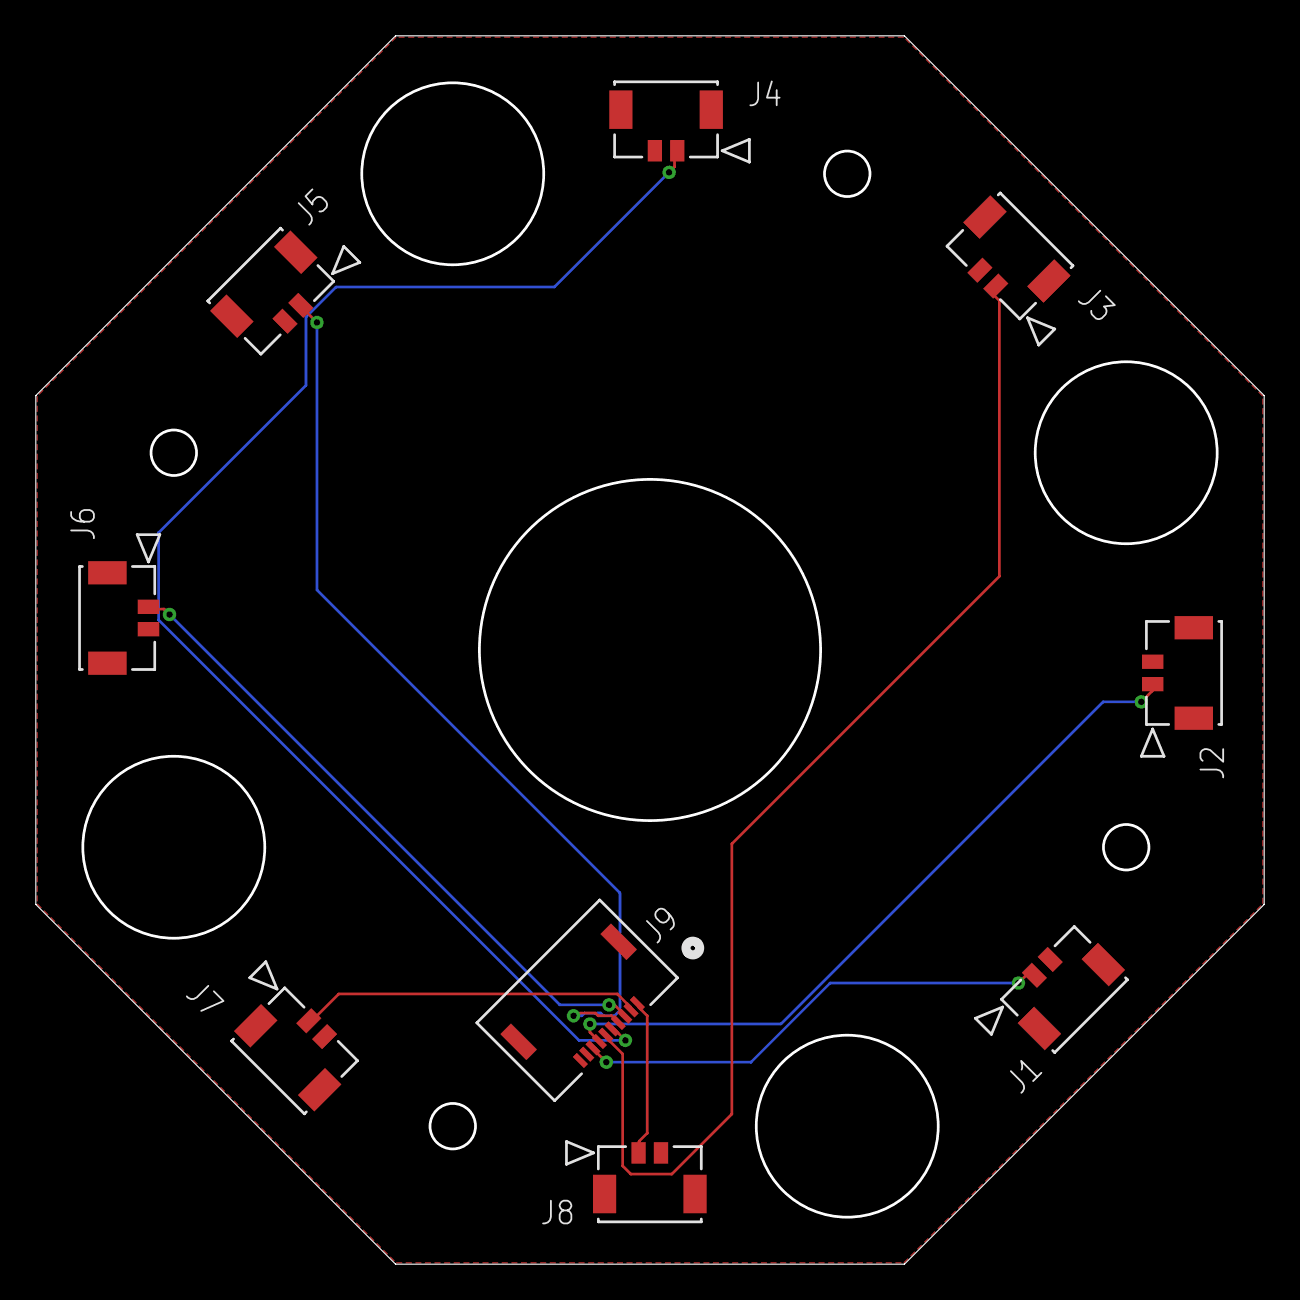
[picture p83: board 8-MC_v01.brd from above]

Board: 2 copper layers, 68.6 x 68.6 mm, 9 parts (0 on the bottom side), 9 nets.

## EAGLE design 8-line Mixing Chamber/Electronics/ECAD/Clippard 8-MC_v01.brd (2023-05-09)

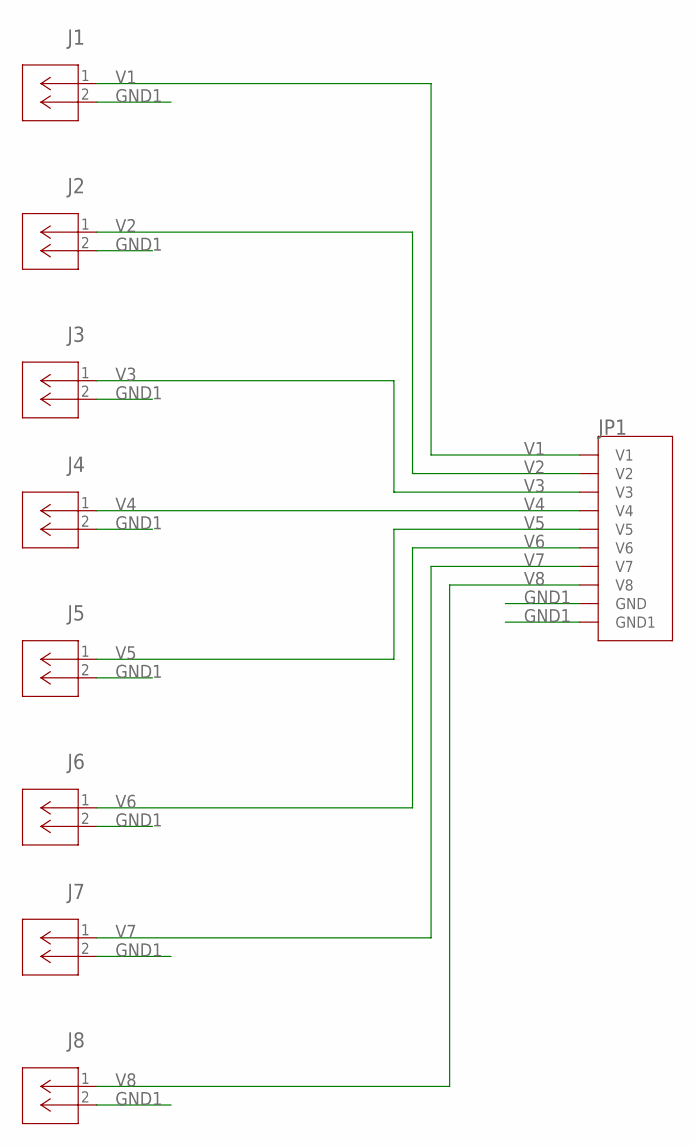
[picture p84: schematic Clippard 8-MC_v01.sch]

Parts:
J1, J2, J3, J4, J5, J6, J7, J8: MOLEX_436500215C; MOLEX_2P_FOOTPRINT_CENTERED
JP1: CONN_10P_TE_1761681-3C; CONN_10P_TE_1761681-3_SE_FOR_V02_CENTERED

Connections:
GND1: J1.2, J2.2, J3.2, J4.2, J5.2, J6.2, J7.2, J8.2, JP1.GND, JP1.GND. (GND1)
V1: J1.1, JP1.V1
V2: J2.1, JP1.V2
V3: J3.1, JP1.V3
V4: J4.1, JP1.V4
V5: J5.1, JP1.V5
V6: J6.1, JP1.V6
V7: J7.1, JP1.V7
V8: J8.1, JP1.V8

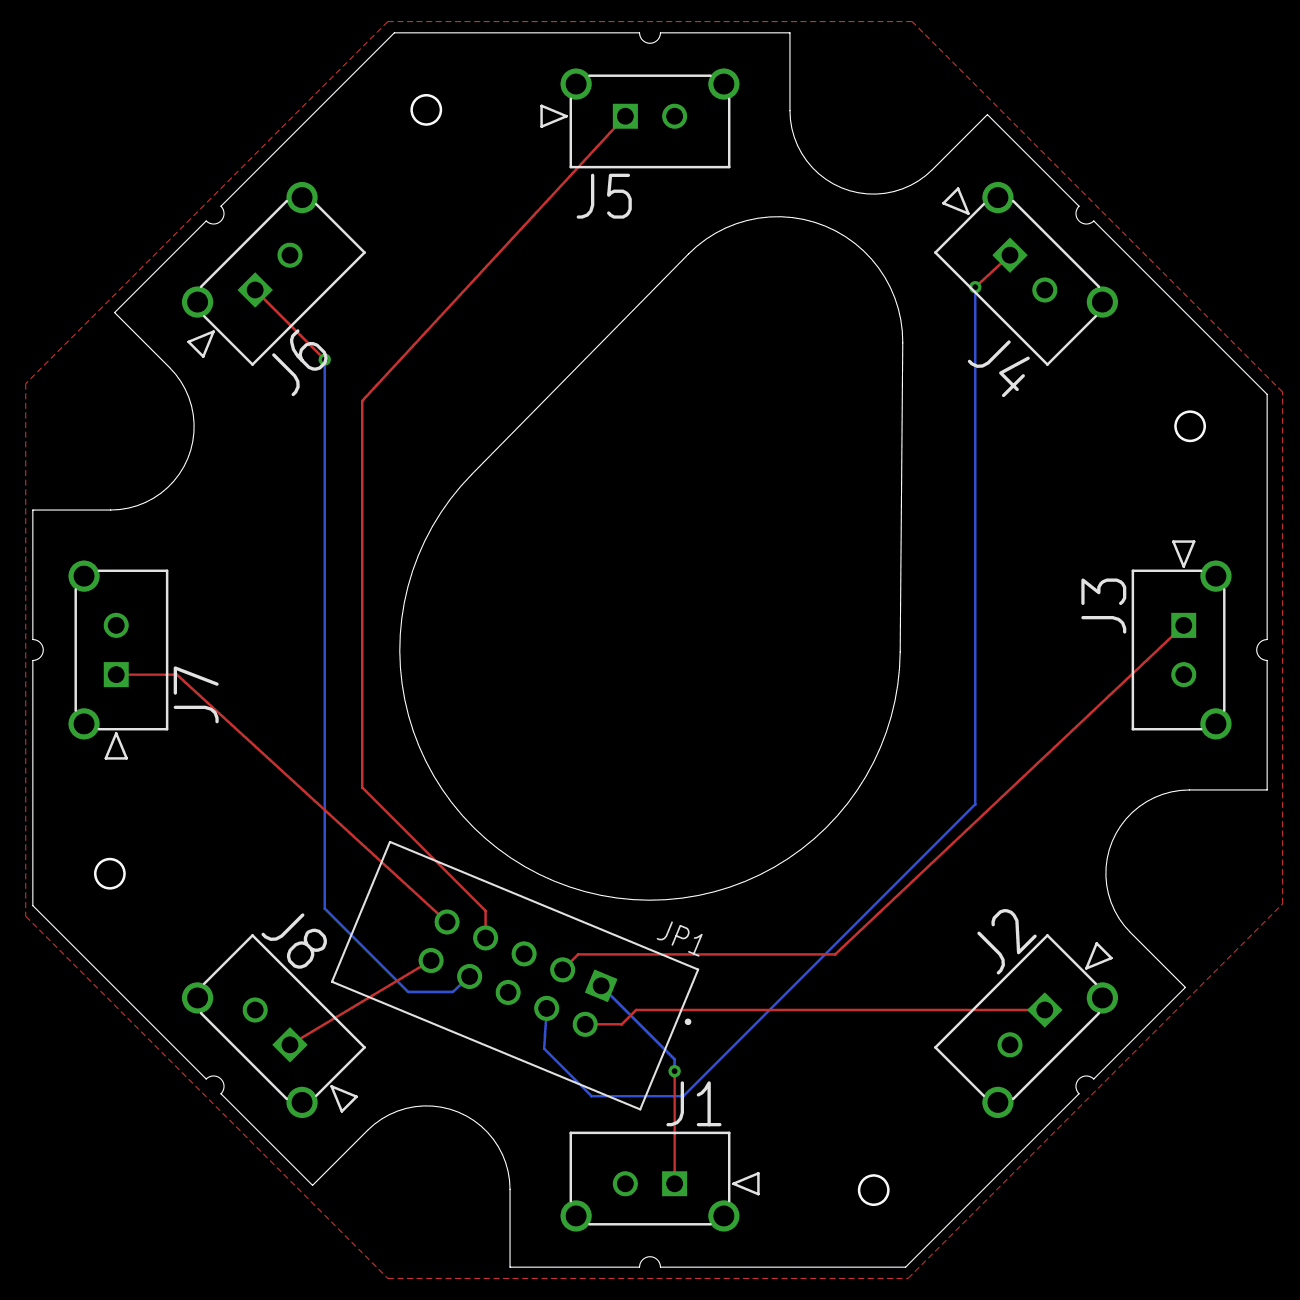
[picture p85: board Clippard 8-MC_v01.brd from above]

Board: 2 copper layers, 75.2 x 75.2 mm, 9 parts (0 on the bottom side), 9 nets.

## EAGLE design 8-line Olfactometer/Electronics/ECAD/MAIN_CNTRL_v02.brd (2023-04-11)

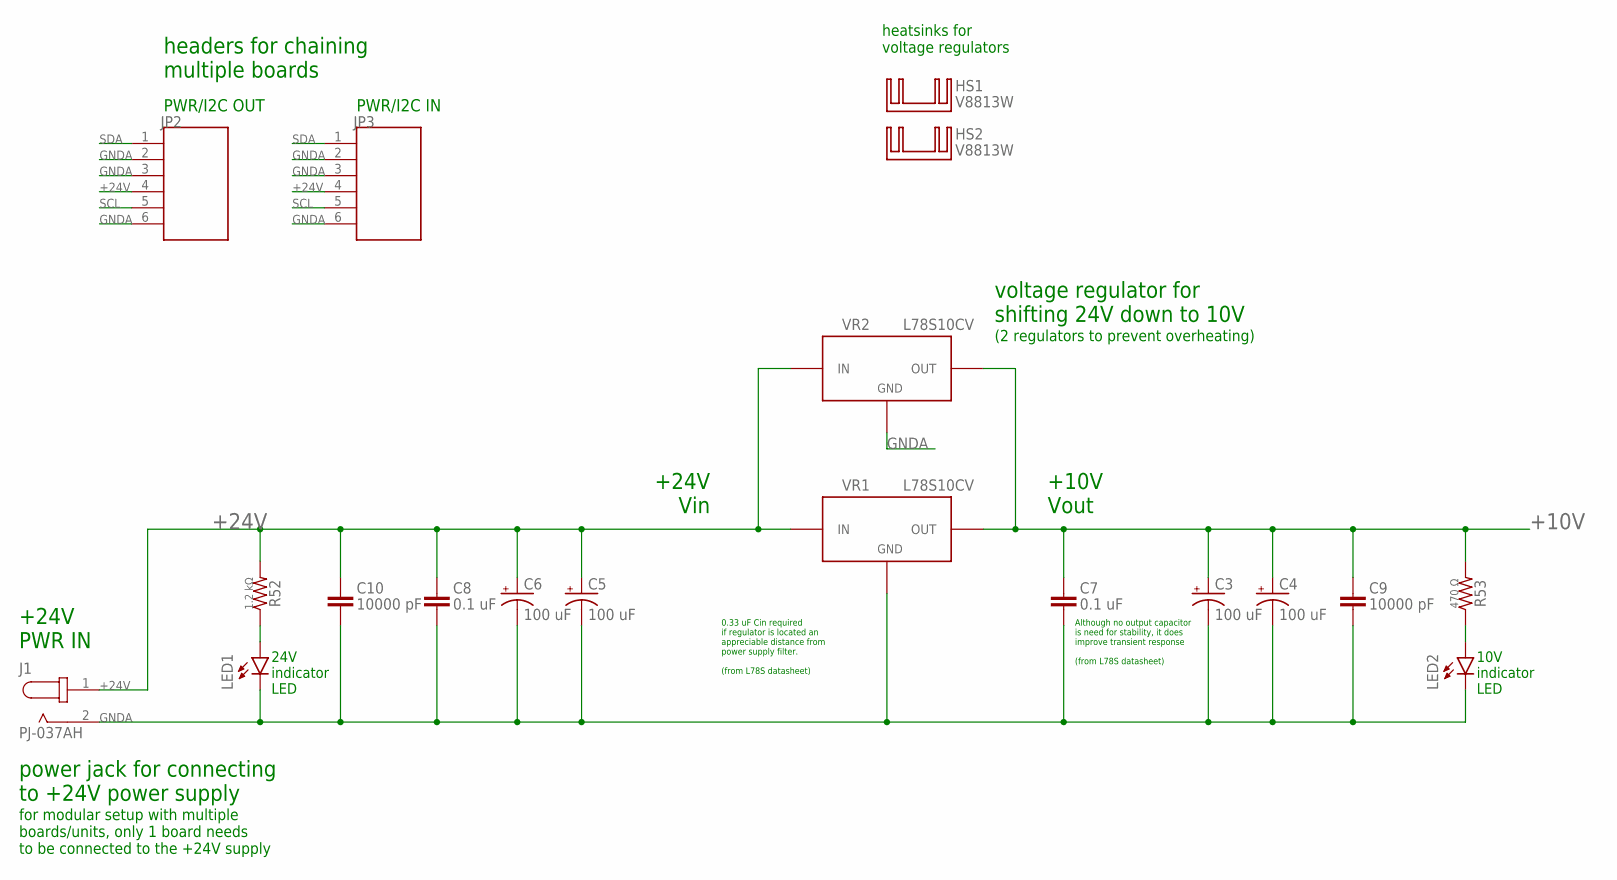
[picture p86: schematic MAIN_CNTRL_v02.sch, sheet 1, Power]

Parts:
C3, C4, C5, C6: 100 uF; CAP_J-V_10X10P5_RUB
C7, C8: 0.1 uF; CAP_1608_TDK
C9, C10: 10000 pF; CAP_1608_TDK
HS1, HS2: V8813W; V8813X
J1: PJ-037AH; CUI_PJ-037AH
JP2, JP3: CONN_06_HEADER; CONN_6P_TE_1761681-1
LED1, LED2: Green LED; LED_VISHAY_VLMX13XX
R52: 1.2 kΩ; RCS0603_REFLOW
R53: 470 Ω; RCS0603_REFLOW
VR1, VR2: L78S10CV

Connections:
+10V: C3.+, C4.+, C7.1, C9.1, R53.2, VR1.3 (OUT), VR2.3 (OUT); also elsewhere on the board
+24V: C5.+, C6.+, C8.1, C10.1, J1.1, JP2.4, JP3.4, R52.2, VR1.1 (IN), VR2.1 (IN); also elsewhere on the board
GNDA: C3.-, C4.-, C5.-, C6.-, C7.2, C8.2, C9.2, C10.2, J1.2, JP2.2, JP2.3, JP2.6, JP3.2, JP3.3, JP3.6, LED1.C, LED2.C, VR1.2 (GND), VR2.2 (GND); also elsewhere on the board
unnamed: LED1.A, R52.1
unnamed: LED2.A, R53.1
SCL: JP2.5, JP3.5; also elsewhere on the board
SDA: JP2.1, JP3.1; also elsewhere on the board

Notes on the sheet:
voltage regulator for shifting 24V down to 10V
+24V Vin
+10V Vout
power jack for connecting to +24V power supply
PWR/I2C IN
24V indicator LED
10V indicator LED
PWR/I2C OUT
+24V PWR IN
for modular setup with multiple boards/units, only 1 board needs to be connected to the +24V supply
Although no output capacitor is need for stability, it does improve transient response (from L78S datasheet)
headers for chaining multiple boards
0.33 uF Cin required if regulator is located an appreciable distance from power supply filter. (from L78S datasheet)
(2 regulators to prevent overheating)
heatsinks for voltage regulators

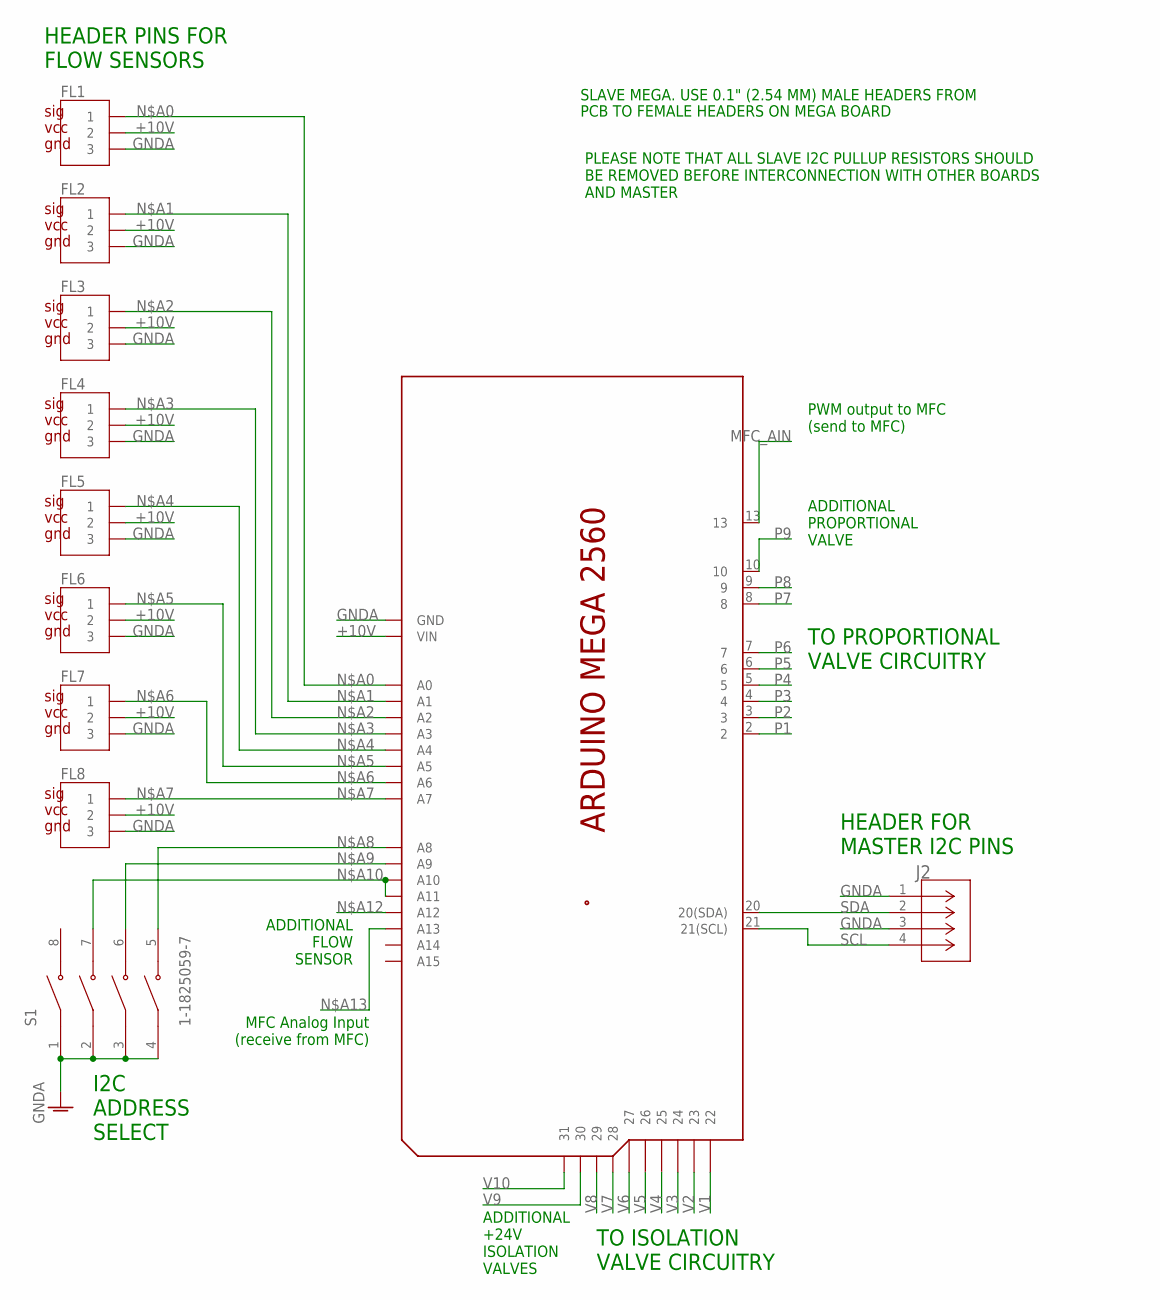
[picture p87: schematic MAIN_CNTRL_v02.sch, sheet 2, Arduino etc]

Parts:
FL1, FL2, FL3, FL4, FL5, FL6, FL7, FL8: CONN_03_FL; 1X03_FL
J2: MOLEX_436500415; MOLEX_4P_FOOTPRINT
S1: 1-1825059-7; SW_1-1825059-7
X1: ARDUINO_MEGA2560_HEADERPINSXX; ARDUINO_MEGA2560_ST_FLIPPED_CUTS

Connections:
+10V: FL1.2, FL2.2, FL3.2, FL4.2, FL5.2, FL6.2, FL7.2, FL8.2, X1.VIN; also elsewhere on the board
GNDA: FL1.3, FL2.3, FL3.3, FL4.3, FL5.3, FL6.3, FL7.3, FL8.3, J2.1, J2.3, S1.1, S1.2, S1.3, S1.4, X1.GND, X1.GND. (GND), X1.GND.. (GND); also elsewhere on the board
MFC_AIN: X1.13; also elsewhere on the board
N$A0: FL1.1, X1.A0
N$A1: FL2.1, X1.A1
N$A2: FL3.1, X1.A2
N$A3: FL4.1, X1.A3
N$A4: FL5.1, X1.A4
N$A5: FL6.1, X1.A5
N$A6: FL7.1, X1.A6
N$A7: FL8.1, X1.A7
N$A8: S1.5, X1.A8
N$A9: S1.6, X1.A9
N$A10: S1.7, X1.A10, X1.A11
N$A12: X1.A12; also elsewhere on the board
N$A13: X1.A13; also elsewhere on the board
P1: X1.2; also elsewhere on the board
P2: X1.3; also elsewhere on the board
P3: X1.4; also elsewhere on the board
P4: X1.5; also elsewhere on the board
P5: X1.6; also elsewhere on the board
P6: X1.7; also elsewhere on the board
P7: X1.8; also elsewhere on the board
P8: X1.9; also elsewhere on the board
P9: X1.10; also elsewhere on the board
SCL: J2.4, X1.21 (21(SCL)); also elsewhere on the board
SDA: J2.2, X1.20 (20(SDA)); also elsewhere on the board
V1: X1.22; also elsewhere on the board
V2: X1.23; also elsewhere on the board
V3: X1.24; also elsewhere on the board
V4: X1.25; also elsewhere on the board
V5: X1.26; also elsewhere on the board
V6: X1.27; also elsewhere on the board
V7: X1.28; also elsewhere on the board
V8: X1.29; also elsewhere on the board
V9: X1.30; also elsewhere on the board
V10: X1.31; also elsewhere on the board

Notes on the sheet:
I2C ADDRESS SELECT
SLAVE MEGA. USE 0.1" (2.54 MM) MALE HEADERS FROM
PCB TO FEMALE HEADERS ON MEGA BOARD
HEADER FOR MASTER I2C PINS
PLEASE NOTE THAT ALL SLAVE I2C PULLUP RESISTORS SHOULD BE REMOVED BEFORE INTERCONNECTION WITH OTHER BOARDS AND MASTER
HEADER PINS FOR FLOW SENSORS
TO PROPORTIONAL VALVE CIRCUITRY
TO ISOLATION VALVE CIRCUITRY
ADDITIONAL FLOW SENSOR
ADDITIONAL +24V ISOLATION VALVES
ADDITIONAL PROPORTIONAL VALVE
MFC Analog Input (receive from MFC)
PWM output to MFC (send to MFC)

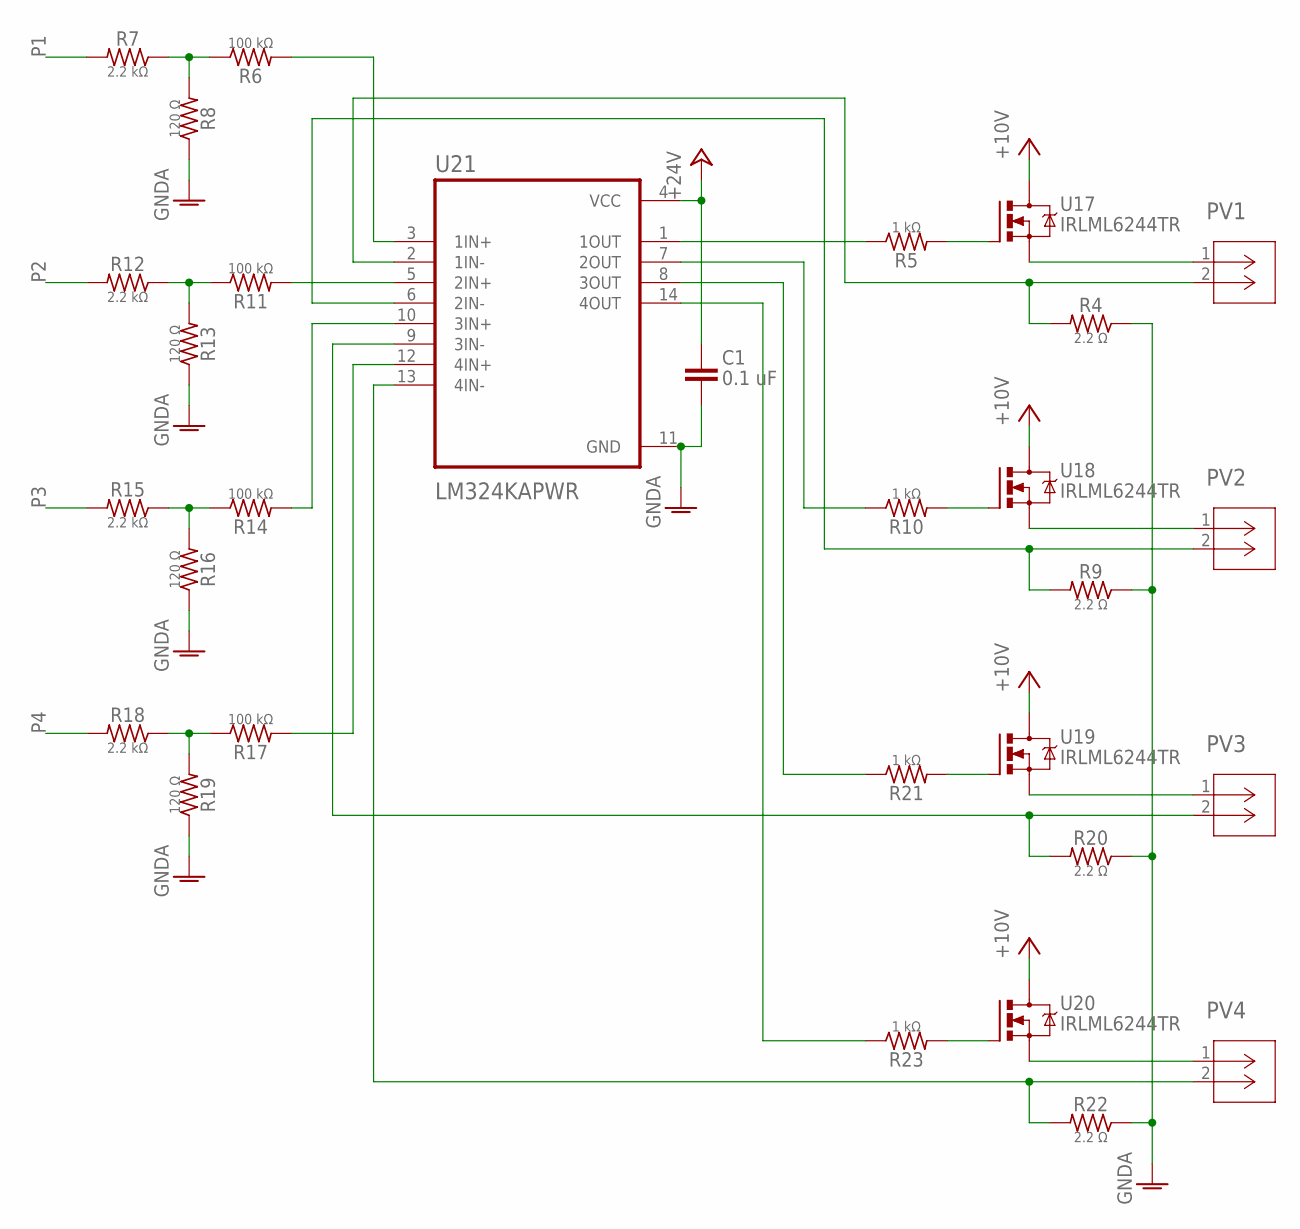
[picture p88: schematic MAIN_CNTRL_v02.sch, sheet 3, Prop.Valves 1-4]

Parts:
C1: 0.1 uF; CAP_1608_TDK
PV1, PV2, PV3, PV4: MOLEX_436500215PVALVES; MOLEX_2P_PVALVES
R4, R9, R20, R22: 2.2 Ω; CRCW1206_E3_REFLOW
R5, R10, R21, R23: 1 kΩ; RES_ERJPA3F1001V
R6, R11, R14, R17: 100 kΩ; RESC1608X55N
R7, R12, R15, R18: 2.2 kΩ; RESC1608X55N
R8, R13, R16, R19: 120 Ω; RCS0603_REFLOW
U17, U18, U19, U20: IRLML6244TR; SOT23
U21: LM324KAPWR; SOP65P640X120-14N

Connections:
+10V: U17.3 (D), U18.3 (D), U19.3 (D), U20.3 (D); also elsewhere on the board
+24V: C1.1, U21.4 (VCC); also elsewhere on the board
GNDA: C1.2, R4.1, R8.1, R9.1, R13.1, R16.1, R19.1, R20.1, R22.1, U21.11 (GND); also elsewhere on the board
unnamed: R6.1, R7.1, R8.2
unnamed: R6.2, U21.3 (1IN+)
unnamed: R5.2, U17.1 (G)
unnamed: R11.1, R12.1, R13.2
unnamed: R11.2, U21.5 (2IN+)
unnamed: R10.2, U18.1 (G)
unnamed: R14.1, R15.1, R16.2
unnamed: R14.2, U21.10 (3IN+)
unnamed: R21.2, U19.1 (G)
unnamed: R17.1, R18.1, R19.2
unnamed: R17.2, U21.12 (4IN+)
unnamed: R23.2, U20.1 (G)
N$PV1_1: PV1.1, U17.2 (S)
N$PV1_2: PV1.2, R4.2, U21.2 (1IN-)
N$PV1_OUT: R5.1, U21.1 (1OUT)
N$PV2_1: PV2.1, U18.2 (S)
N$PV2_2: PV2.2, R9.2, U21.6 (2IN-)
N$PV2_OUT: R10.1, U21.7 (2OUT)
N$PV3_1: PV3.1, U19.2 (S)
N$PV3_2: PV3.2, R20.2, U21.9 (3IN-)
N$PV3_OUT: R21.1, U21.8 (3OUT)
N$PV4_1: PV4.1, U20.2 (S)
N$PV4_2: PV4.2, R22.2, U21.13 (4IN-)
N$PV4_OUT: R23.1, U21.14 (4OUT)
P1: R7.2; also elsewhere on the board
P2: R12.2; also elsewhere on the board
P3: R15.2; also elsewhere on the board
P4: R18.2; also elsewhere on the board

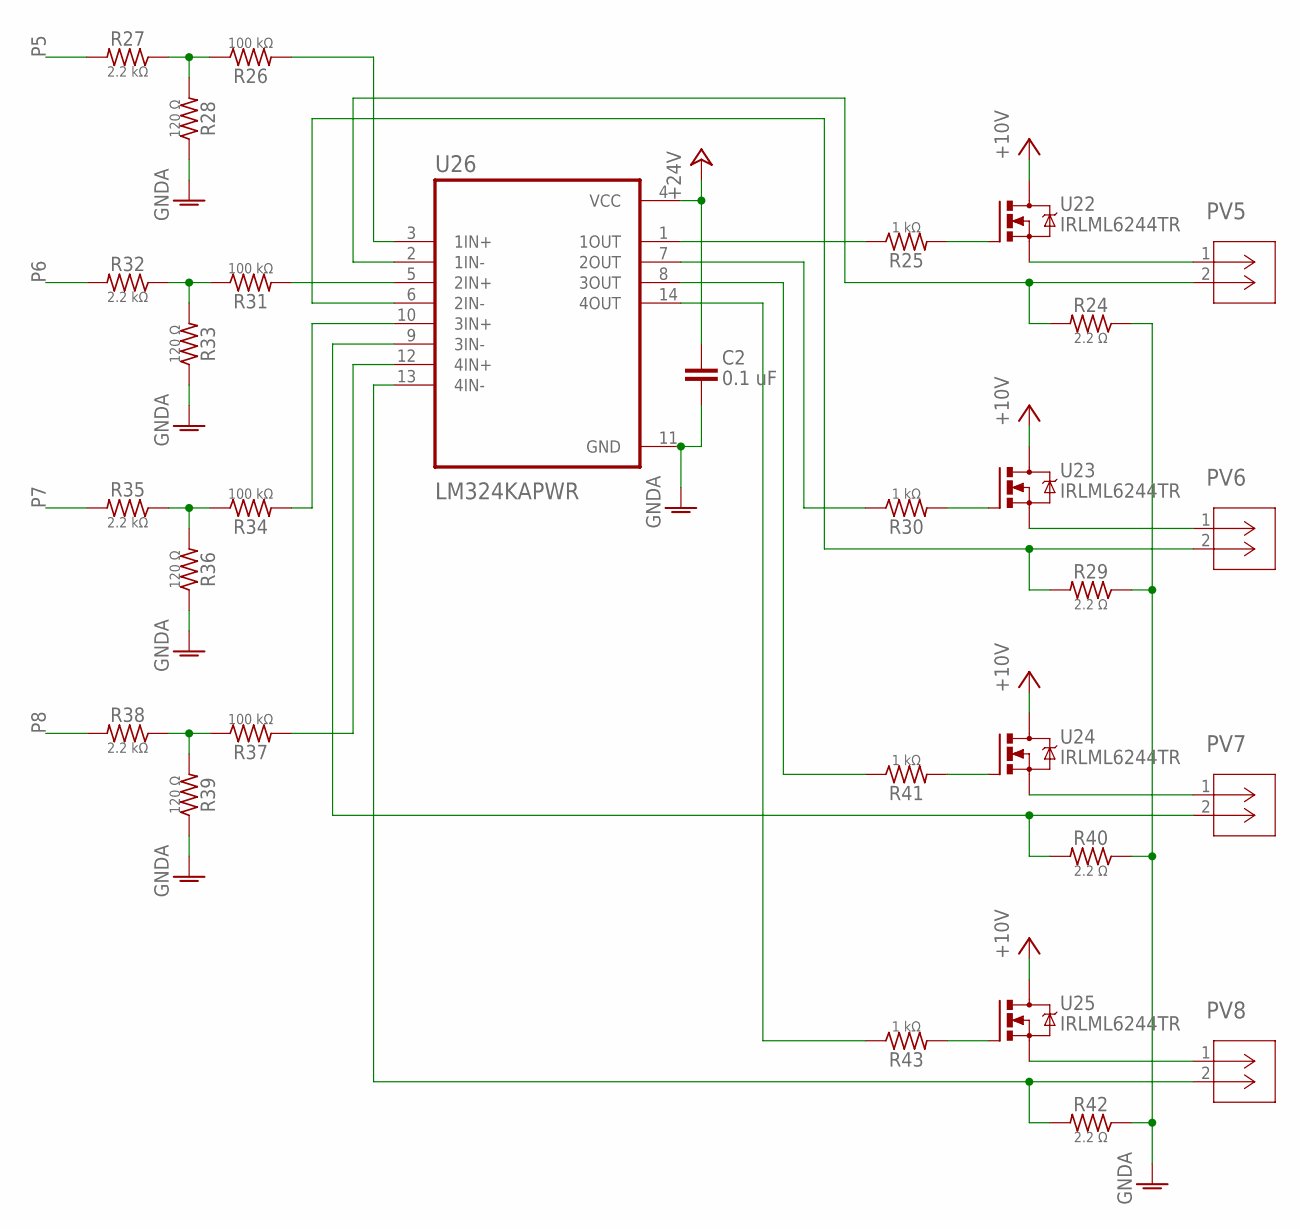
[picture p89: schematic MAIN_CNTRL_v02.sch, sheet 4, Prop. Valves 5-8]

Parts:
C2: 0.1 uF; CAP_1608_TDK
PV5, PV6, PV7, PV8: MOLEX_436500215PVALVES; MOLEX_2P_PVALVES
R24, R29, R40, R42: 2.2 Ω; CRCW1206_E3_REFLOW
R25, R30, R41, R43: 1 kΩ; RES_ERJPA3F1001V
R26, R31, R34, R37: 100 kΩ; RESC1608X55N
R27, R32, R35, R38: 2.2 kΩ; RESC1608X55N
R28, R33, R36, R39: 120 Ω; RCS0603_REFLOW
U22, U23, U24, U25: IRLML6244TR; SOT23
U26: LM324KAPWR; SOP65P640X120-14N

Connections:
+10V: U22.3 (D), U23.3 (D), U24.3 (D), U25.3 (D); also elsewhere on the board
+24V: C2.1, U26.4 (VCC); also elsewhere on the board
GNDA: C2.2, R24.1, R28.1, R29.1, R33.1, R36.1, R39.1, R40.1, R42.1, U26.11 (GND); also elsewhere on the board
unnamed: R26.1, R27.1, R28.2
unnamed: R26.2, U26.3 (1IN+)
unnamed: R25.2, U22.1 (G)
unnamed: R31.1, R32.1, R33.2
unnamed: R31.2, U26.5 (2IN+)
unnamed: R30.2, U23.1 (G)
unnamed: R34.1, R35.1, R36.2
unnamed: R34.2, U26.10 (3IN+)
unnamed: R41.2, U24.1 (G)
unnamed: R37.1, R38.1, R39.2
unnamed: R37.2, U26.12 (4IN+)
unnamed: R43.2, U25.1 (G)
N$PV5_1: PV5.1, U22.2 (S)
N$PV5_2: PV5.2, R24.2, U26.2 (1IN-)
N$PV5_OUT: R25.1, U26.1 (1OUT)
N$PV6_1: PV6.1, U23.2 (S)
N$PV6_2: PV6.2, R29.2, U26.6 (2IN-)
N$PV6_OUT: R30.1, U26.7 (2OUT)
N$PV7_1: PV7.1, U24.2 (S)
N$PV7_2: PV7.2, R40.2, U26.9 (3IN-)
N$PV7_OUT: R41.1, U26.8 (3OUT)
N$PV8_1: PV8.1, U25.2 (S)
N$PV8_2: PV8.2, R42.2, U26.13 (4IN-)
N$PV8_OUT: R43.1, U26.14 (4OUT)
P5: R27.2; also elsewhere on the board
P6: R32.2; also elsewhere on the board
P7: R35.2; also elsewhere on the board
P8: R38.2; also elsewhere on the board

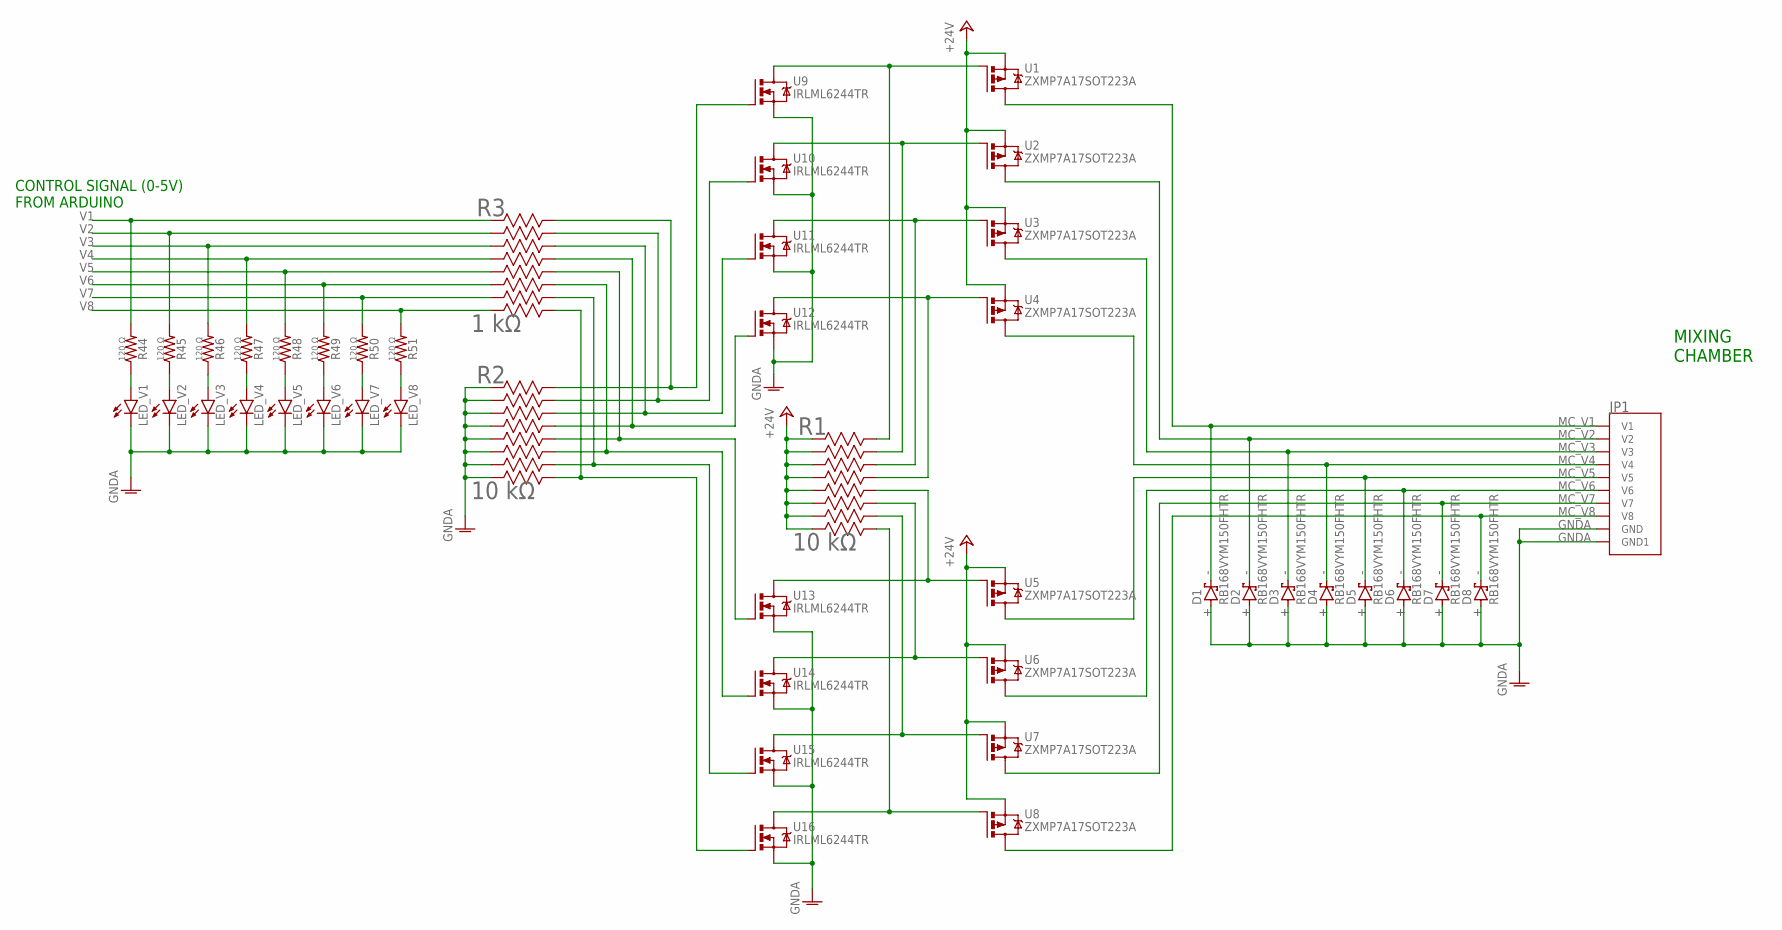
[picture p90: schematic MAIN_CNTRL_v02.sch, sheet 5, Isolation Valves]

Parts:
D1, D2, D3, D4, D5, D6, D7, D8: RB168VYM150FHTR; DIO_RB160VAM_ROM
JP1: CONN_10P_CUSTOM_N2510-6002RBV02; CONN_10P_TE_1761681-3_SE_FOR_V02
LED_V1, LED_V2, LED_V3, LED_V4, LED_V5, LED_V6, LED_V7, LED_V8: Blue LED; LED_VISHAY_VLMX13XX
R1, R2: 10 kΩ; BO_4816P
R3: 1 kΩ; BO_4816P
R44, R45, R46, R47, R48, R49, R50, R51: 120 Ω; RCS0603_REFLOW
U1, U2, U3, U4, U5, U6, U7, U8: ZXMP7A17SOT223A; SOT223
U9, U10, U11, U12, U13, U14, U15, U16: IRLML6244TR; SOT23

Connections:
+24V: R1.1, R1.2, R1.3, R1.4, R1.5, R1.6, R1.7, R1.8, U1.3 (S), U2.3 (S), U3.3 (S), U4.3 (S), U5.3 (S), U6.3 (S), U7.3 (S), U8.3 (S); also elsewhere on the board
GNDA: D1.2 (A), D2.2 (A), D3.2 (A), D4.2 (A), D5.2 (A), D6.2 (A), D7.2 (A), D8.2 (A), JP1.GND, JP1.GND. (GND1), LED_V1.C, LED_V2.C, LED_V3.C, LED_V4.C, LED_V5.C, LED_V6.C, LED_V7.C, LED_V8.C, R2.1, R2.2, R2.3, R2.4, R2.5, R2.6, R2.7, R2.8, U9.2 (S), U10.2 (S), U11.2 (S), U12.2 (S), U13.2 (S), U14.2 (S), U15.2 (S), U16.2 (S); also elsewhere on the board
MC_V1: D1.1 (C), JP1.V1, U1.2 (D), U1.4 (D)
MC_V2: D2.1 (C), JP1.V2, U2.2 (D), U2.4 (D)
MC_V3: D3.1 (C), JP1.V3, U3.2 (D), U3.4 (D)
MC_V4: D4.1 (C), JP1.V4, U4.2 (D), U4.4 (D)
MC_V5: D5.1 (C), JP1.V5, U5.2 (D), U5.4 (D)
MC_V6: D6.1 (C), JP1.V6, U6.2 (D), U6.4 (D)
MC_V7: D7.1 (C), JP1.V7, U7.2 (D), U7.4 (D)
MC_V8: D8.1 (C), JP1.V8, U8.2 (D), U8.4 (D)
unnamed: R1.16, U1.1 (G), U9.3 (D)
unnamed: R2.16, R3.16, U9.1 (G)
unnamed: R1.15, U2.1 (G), U10.3 (D)
unnamed: R2.15, R3.15, U10.1 (G)
unnamed: R1.14, U3.1 (G), U11.3 (D)
unnamed: R2.14, R3.14, U11.1 (G)
unnamed: R1.13, U4.1 (G), U12.3 (D)
unnamed: R2.13, R3.13, U12.1 (G)
unnamed: R1.12, U5.1 (G), U13.3 (D)
unnamed: R2.12, R3.12, U13.1 (G)
unnamed: R1.11, U6.1 (G), U14.3 (D)
unnamed: R2.11, R3.11, U14.1 (G)
unnamed: R1.10, U7.1 (G), U15.3 (D)
unnamed: R2.10, R3.10, U15.1 (G)
unnamed: R1.9, U8.1 (G), U16.3 (D)
unnamed: R2.9, R3.9, U16.1 (G)
N$LED1: LED_V1.A, R44.1
N$LED2: LED_V2.A, R45.1
N$LED3: LED_V3.A, R46.1
N$LED4: LED_V4.A, R47.1
N$LED5: LED_V5.A, R48.1
N$LED6: LED_V6.A, R49.1
N$LED7: LED_V7.A, R50.1
N$LED8: LED_V8.A, R51.1
V1: R3.1, R44.2; also elsewhere on the board
V2: R3.2, R45.2; also elsewhere on the board
V3: R3.3, R46.2; also elsewhere on the board
V4: R3.4, R47.2; also elsewhere on the board
V5: R3.5, R48.2; also elsewhere on the board
V6: R3.6, R49.2; also elsewhere on the board
V7: R3.7, R50.2; also elsewhere on the board
V8: R3.8, R51.2; also elsewhere on the board

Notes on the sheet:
MIXING CHAMBER
CONTROL SIGNAL (0-5V) FROM ARDUINO

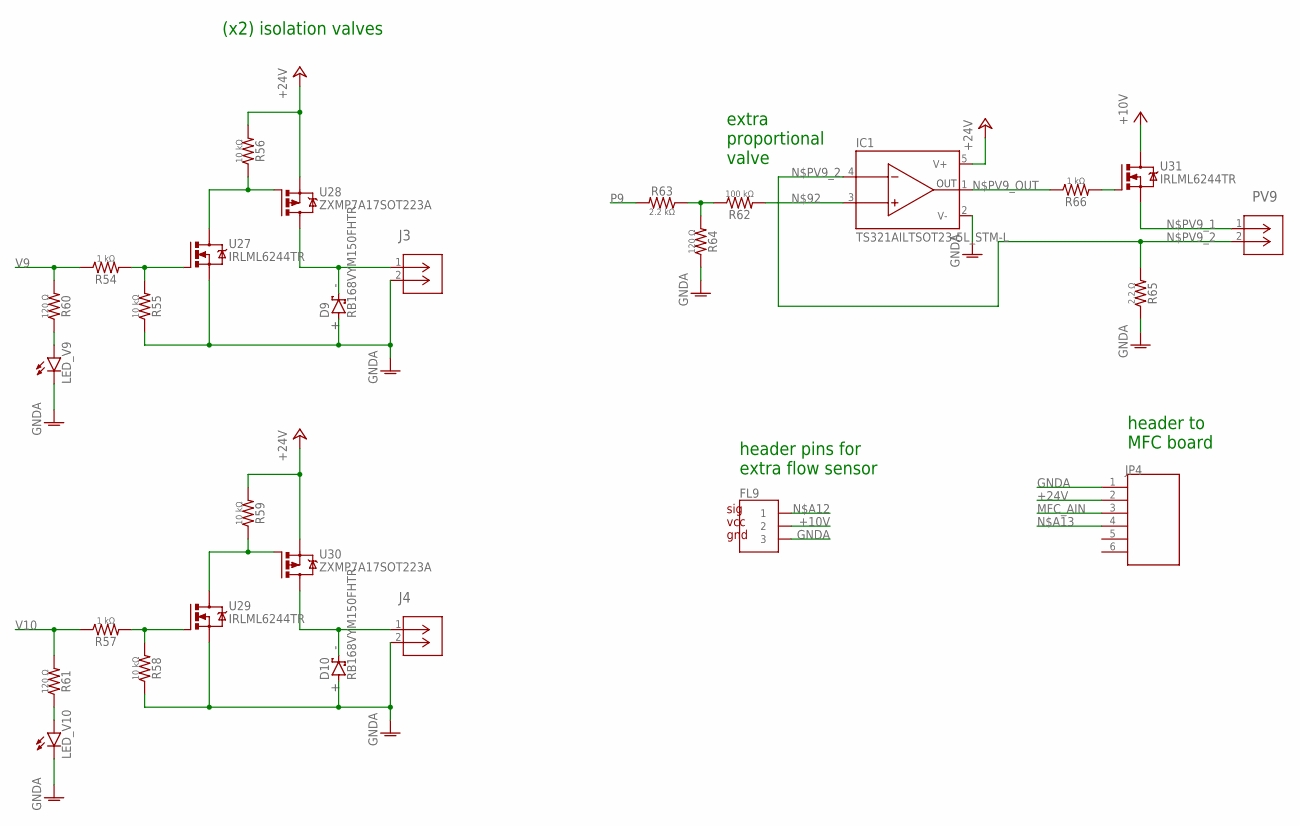
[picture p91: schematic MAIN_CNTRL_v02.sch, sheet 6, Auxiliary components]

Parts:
D9, D10: RB168VYM150FHTR; DIO_RB160VAM_ROM
FL9: CONN_03_FL; 1X03_FL
IC1: TS321AILTSOT23-5L_STM-L; SOT23-5L_STM-L
J3, J4: MOLEX_436500215; MOLEX_2P_FOOTPRINT
JP4: CONN_06_HEADER; CONN_6P_TE_1761681-1
LED_V9, LED_V10: Blue LED; LED_VISHAY_VLMX13XX
PV9: MOLEX_436500215PVALVES; MOLEX_2P_PVALVES
R54, R57, R66: 1 kΩ; RES_ERJPA3F1001V
R55, R56, R58, R59: 10 kΩ; RES_ERJPA3F1001V
R60, R61, R64: 120 Ω; RCS0603_REFLOW
R62: 100 kΩ; RESC1608X55N
R63: 2.2 kΩ; RESC1608X55N
R65: 2.2 Ω; CRCW1206_E3_REFLOW
U27, U29, U31: IRLML6244TR; SOT23
U28, U30: ZXMP7A17SOT223A; SOT223

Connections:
+10V: FL9.2, U31.3 (D); also elsewhere on the board
+24V: IC1.5 (V+), JP4.2, R56.2, R59.2, U28.3 (S), U30.3 (S); also elsewhere on the board
GNDA: D9.2 (A), D10.2 (A), FL9.3, IC1.2 (V-), J3.2, J4.2, JP4.1, LED_V9.C, LED_V10.C, R55.1, R58.1, R64.1, R65.1, U27.2 (S), U29.2 (S); also elsewhere on the board
MFC_AIN: JP4.3; also elsewhere on the board
unnamed: R56.1, U27.3 (D), U28.1 (G)
unnamed: R54.2, R55.2, U27.1 (G)
unnamed: R59.1, U29.3 (D), U30.1 (G)
unnamed: R57.2, R58.2, U29.1 (G)
unnamed: R62.1, R63.1, R64.2
unnamed: IC1.3 (+IN), R62.2
unnamed: R66.2, U31.1 (G)
N$A12: FL9.1; also elsewhere on the board
N$A13: JP4.4; also elsewhere on the board
N$LED9: LED_V9.A, R60.1
N$LED10: LED_V10.A, R61.1
N$PV9_1: PV9.1, U31.2 (S)
N$PV9_2: IC1.4 (-IN), PV9.2, R65.2
N$PV9_OUT: IC1.1 (OUT), R66.1
N$V9: D9.1 (C), J3.1, U28.2 (D), U28.4 (D)
N$V10: D10.1 (C), J4.1, U30.2 (D), U30.4 (D)
P9: R63.2; also elsewhere on the board
V9: R54.1, R60.2; also elsewhere on the board
V10: R57.1, R61.2; also elsewhere on the board

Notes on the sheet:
header pins for extra flow sensor
(x2) isolation valves
extra proportional valve
header to MFC board

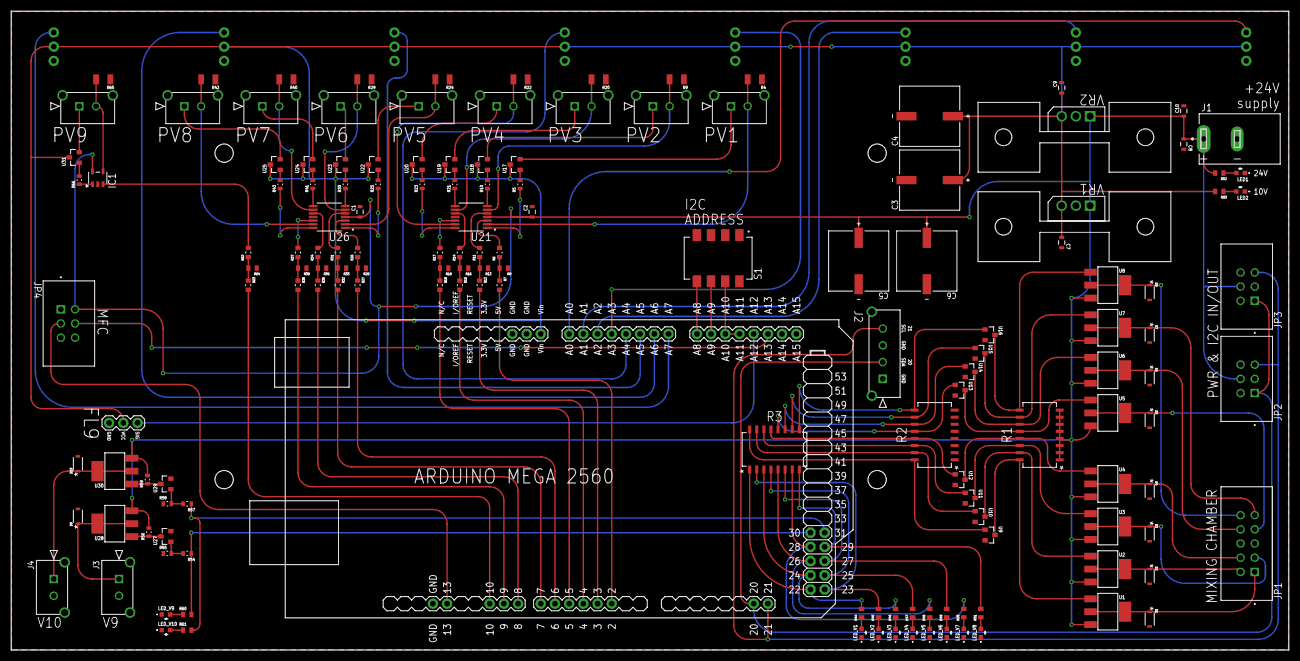
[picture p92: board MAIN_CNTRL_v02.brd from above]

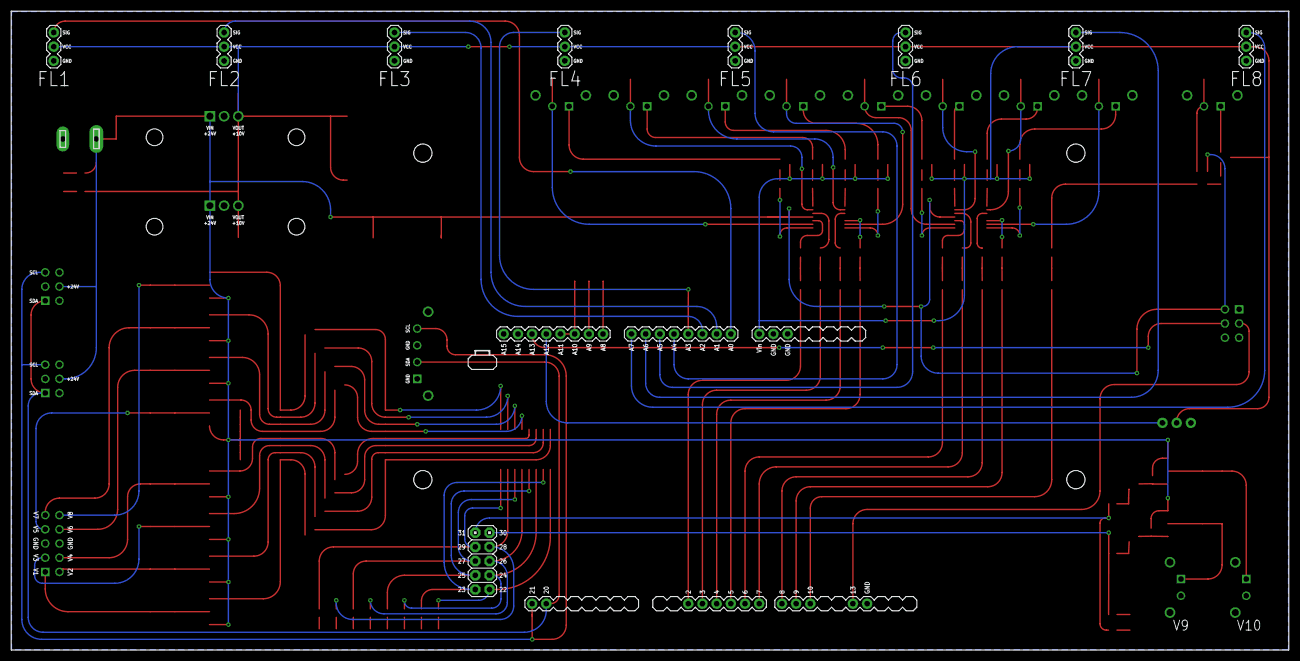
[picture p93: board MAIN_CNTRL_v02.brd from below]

Board: 2 copper layers, 228.6 x 114.3 mm, 162 parts (8 on the bottom side), 134 nets.

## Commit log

2023-04-11 renamed folder
    [copper_bottom.gbr, copper_top.gbr, drill_1_16.xln, gerber_job.gbrjob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]
2023-04-11 updated to version 2
    [MAIN_CNTRL_v01.brd, MAIN_CNTRL_v01.sch, MAIN_CNTRL_v02.brd, MAIN_CNTRL_v02.sch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]
2023-04-11 initial commit - BOM for MAIN_CNTRL v01
    [MAIN_CNTRL_BOM.xlsx]
2023-04-12 initial commit: 3D PCB with silkscreen
    [MAIN CNTRL_v02 Bottom.ipt, MAIN CNTRL_v02 Top.ipt]
2023-04-12 folder relocation
    [MAIN CNTRL_v02 Bottom.ipt, MAIN CNTRL_v02 Top.ipt]
2023-04-14 initial commit - hardware files for v01
    [main_manifold_8v_01.dwg, main_manifold_8v_01.stp, main_manifold_cover_1v_01.dwg, main_manifold_cover_1v_01.stp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]
2023-04-18 created separate Electronics folder
    [MAIN_CNTRL_BOM.xlsx, MAIN_CNTRL_v02.brd, MAIN_CNTRL_v02.sch, copper_bottom.gbr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]
2023-04-18 moved 3D PCB files to Electronics folder
    [1-soldermask.ipt, 16-soldermask.ipt, 1761681-3 v1.ipt, 1X01_maleheader v1.ipt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]
2023-04-18 folder reorg
    [MAIN_CNTRL_v02.brd, MAIN_CNTRL_v02.sch]
2023-04-18 initial commit - .ipt files for hardware
    [main_manifold_8v.ipt, main_manifold_cover_1v.ipt, top_cover.ipt]
2023-04-18 renamed v01 .ipt files
    [main_manifold_8v_v01.ipt, main_manifold_cover_1v_v01.ipt, top_cover_v01.ipt]
2023-05-08 reorganized mixing chamber directories; separated Lee and Clippard designs into differed directories
    [8-MC_v01.brd, 8-MC_v01.sch, Clippard 8-MC cover_v01.step, Clippard 8-MC heart_v01.step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]
2023-05-09 initial upload of Clippard 8-MC Electronics files
    [Clippard 8-MC_v01.brd, Clippard 8-MC_v01.sch, copper_bottom.gbr, copper_top.gbr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]
2023-05-09 initial commit of Lee 8-MC Electronics files for manufacturing
    [copper_bottom.gbr, copper_top.gbr, drill_1_16.xln, gerber_job.gbrjob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]
2023-05-09 upload of Clippard & Lee BOMs
    [Clippard 8-MC BOM.xlsx, Lee 8-MC BOM.xlsx]
2023-05-18 added 3D PCB image to Olfa Electronics readme
2023-05-18 fixed error in olfa 3D PCB image
2023-10-03 initial commit of Arduino holder
    [Arduino_holder.ipt, Arduino_holder.stl]
2023-10-03 initial commit
    10-24 nut for Clippard 8-MC (v01)
    [Nut for Precision Compression Fitting 10-24.ipt, Nut for Precision Compression Fitting 10-24.stp]
2023-11-20 initial commit - first draft of Clippard assembly instructions
2023-11-20 initial commit - first draft of olfactometer assembly instructions
2023-11-28 Add files via upload
    initial commit of vialHolder files
    [vialHolder_2v.ipt, vialHolder_2v.stl]
2023-11-29 Add files via upload
    initial commit of mainPlate
    [mainPlate.ipt, mainPlate.stl]
2023-11-29 Add files via upload
    initial commit of full assembly image
2023-12-09 folder organization
    [main_manifold_8v_v02.ipt, main_manifold_cover_1v_v02.ipt, top_cover_02.ipt]
2024-01-05 Updated mount_bracket parts
    [mount_bracket 8020_1515.ipt, mount_bracket 8020_1515.stl, mount_bracket item_5.ipt, mount_bracket item_5.stl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]
2024-01-26 3D printed parts: initial commit of Arduino holder & vialHolder
    [Arduino_holder.ipt, Arduino_holder.stl, vialHolder_2v.ipt, vialHolder_2v.stl]
2024-01-26 Olfa 3D printed parts: initial commit of new mount parts, organization of various mounting parts within folder
    [mount_bracket 8020_1515.ipt, mount_bracket 8020_1515.stl, mount_bracket 8020_1515_withhole.ipt, mount_bracket 8020_1515_withhole.stl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]
2024-01-26 Olfa manufacturing: restore files that were accidentally deleted on previous folder reorg (12/11/23)
    [main_manifold_8v_v02.ipt, main_manifold_8v_v02.stp, main_manifold_cover_1v_v02.ipt, main_manifold_cover_1v_v02.stp]
2024-01-26 Olfa manufacturing: folder reorg
    [main_manifold_8v_v02.ipt, main_manifold_8v_v02.stp, main_manifold_cover_1v_v02.ipt, main_manifold_cover_1v_v02.stp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]
2024-01-26 Clippard MC: folder reorg
    [Clippard 8-MC cover_v01.step, Clippard 8-MC heart_v01.step]
2024-02-27 Clippard 8-MC: initial commit of .ipt CAD files
    [Clippard 8-MC cover_v01.ipt, Clippard 8-MC heart_v01.ipt]
2024-02-27 Clippard 8-MC: recreated .ipt CAD files in Inventor
    [Clippard 8-MC cover_v01.ipt, Clippard 8-MC heart_v01.ipt]
2024-03-11 Olfa assembly instructions: test upload for inserting pictures into document
2024-03-11 Olfa assembly instructions: updates for clarity
2024-03-12 Olfa: test upload of flow calibration protocol
2024-03-18 Olfa 3D printed parts: updated version of vialHolder
    Adds stabilizing piece under main plate
    [vialHolder_2v.ipt, vialHolder_2v.stl]
2024-03-18 Olfa Assembly Instructions: further updates with images
2024-03-21 Mixing Chamber: initial commit of README for output fitting
2024-03-21 Mixing Chamber: update to README for output fitting
2024-03-21 Olfa: reorganized folder
    [main_manifold_8v_v02.ipt, main_manifold_8v_v02.stp, main_manifold_cover_1v_v02.ipt, main_manifold_cover_1v_v02.stp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]
2024-03-21 Clippard MC: reorganized folder
    [Clippard 8-MC cover_v01.ipt, Clippard 8-MC cover_v01.step, Clippard 8-MC heart_v01.ipt, Clippard 8-MC heart_v01.step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]
2024-03-22 Mixing Chamber: uploaded hardware & PCB images, 3D PCB files
    [1-copper.ipt, 1-soldermask.ipt, 16-copper.ipt, 16-soldermask.ipt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]
2024-03-22 Mixing Chamber: reorg
2024-03-22 Mixing Chamber: image upload
2024-03-22 Mixing Chamber: fix to error in Electronics readme
2024-03-22 Mixing Chamber: ACTUAL fix to error in Electronics readme
    previous commit was update to Olfactometer\Electronics readme (added PCB assembly instructions)
2024-03-22 Mixing Chamber: updated to correct versions of v01 .ipt files
    [Clippard 8-MC cover_v01.ipt, Clippard 8-MC heart_v01.ipt]
2024-05-13 Clippard 8-MC hardware updated to version 2
    [Clippard 8-MC cover v2A.dwg, Clippard 8-MC cover v2A.ipt, Clippard 8-MC cover v2A.stl, Clippard 8-MC cover v2A.stp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]
2024-06-14 Updated flow sensor calibration protocol
2024-06-14 inital commit of olfactometer BOM draft
    [8-line olfa hardware BOM.xlsx]
2024-06-18 Fix to flow sensor calibration protocol example calibration table image
2024-06-21 Reorganized Mixing Chamber directory
    [1-copper.ipt, 1-soldermask.ipt, 16-copper.ipt, 16-soldermask.ipt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]
2024-06-21 Moved Mixing Chamber schematics from main directory to Mixing Chamber folder
2024-06-26 Minor updates to air flow schematics
    Main schematic now includes Alicat MFC & needle valve
2024-07-13 Updated flow sensor calibration protocol
    Now includes instructions for calibrating while flow sensors installed on olfa manifold
2024-07-13 Updated flow sensor calibration protocol
    Minor formatting edits
2024-07-16 Updates to Flow Sensor Calibration Protocol
    Added example config file (for updating once calibration is complete)
    Added some clarifying details to protocol
2024-07-16 Updated Flow Sensor Calibration Protocol
    Formatting edits
2024-08-23 Updated olfa assembly instructions: added images of vial holder assembly
    also some minor formatting edits
2024-09-03 Updated Mixing Chamber assembly instructions
    Added images for connecting cover to heart
2024-09-03 Updated Olfactometer assembly instructions
    Added images for assembling vial holders & PCB
2024-09-03 Formatting updates to flow sensor calibration protocol
2024-09-17 Updated Flow Sensor Calibration schematic
    Moved calibration images to separate folder; minor formatting updates to calibration protocol
2024-09-27 Updated MC assembly instructions: Added images for attaching PCB to cover
2024-10-14 Updated Olfactometer BOM
    [8-line olfa hardware BOM.xlsx]
2024-10-15 Flow Sensor Calibration Protocol: minor clarifying edits & schematic update
2024-11-19 Upload of Clippard 8-MC BOM
    [Clippard 8-MC BOM.xlsx]
2024-12-20 Reorganized Olfactometer Hardware directories
    [Arduino_holder.ipt, Arduino_holder.stl, mainPlate.ipt, mainPlate.stl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]
2025-05-07 Olfa PCB BOM: renamed to v02
    [MAIN_CNTRL_BOM_v02.xlsx]
2025-05-09 Minor assembly instruction updates (to clear git queue)
2025-05-09 General organization
    MC: Moved ECAD to its own folder, committed non-changes to hardware files (to clear git queue)
    Olfactometer: Committed non-changes to 3D PCB (to clear git queue)
    [Clippard 8-MC cover v2A.ipt, Clippard 8-MC heart v2A.ipt]
2025-05-13 Olfa 3D printed parts: Updated vialHolder (slightly shorter, larger cutout for fitting tubing through)
    [vialHolder_2v_02.ipt, vialHolder_2v_02.stl]
2025-05-13 Olfa: Cleaned 3D printed parts folder
    [vialHolder_2v_01.ipt, vialHolder_2v_01.stl]
2025-05-15 Olfa: Updated documentation for mounting components
    Added images of setup types, temporarily removed the CAD files for the 'sliding only' parts
    [mount_bracket 8020_1515.ipt, mount_bracket 8020_1515.stl, mount_bracket 8020_1515_withhole.ipt, mount_bracket 8020_1515_withhole.stl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]

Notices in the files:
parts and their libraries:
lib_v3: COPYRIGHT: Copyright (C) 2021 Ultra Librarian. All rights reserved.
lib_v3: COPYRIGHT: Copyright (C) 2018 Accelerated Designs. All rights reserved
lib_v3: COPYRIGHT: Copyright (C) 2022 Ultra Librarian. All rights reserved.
